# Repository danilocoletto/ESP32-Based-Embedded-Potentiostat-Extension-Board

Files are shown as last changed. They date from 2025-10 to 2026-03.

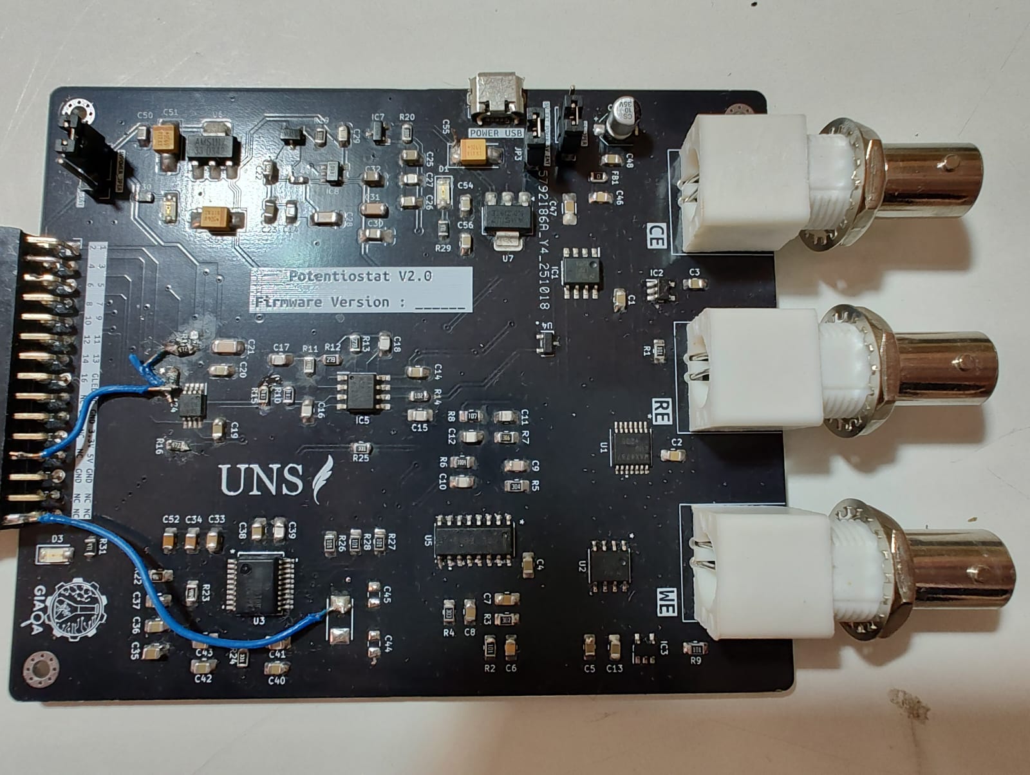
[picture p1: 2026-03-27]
Images&Schematics/Images/Potentiostat_PCB2.jpeg

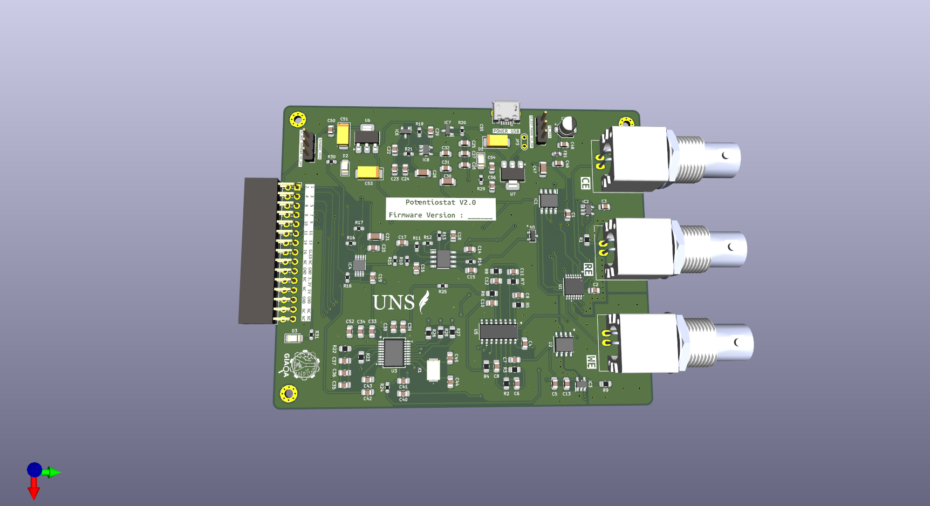
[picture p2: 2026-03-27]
Images&Schematics/Renders/Potenciostato_v2.0_1.png

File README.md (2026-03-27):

# ESP32-Based Real-Time Embedded Potentiostat Extension Board





> **⚠️ PROJECT STATUS: ONGOING**
> This project is currently under active development. The hardware design and firmware are subject to changes. Please check the `dev` branch for the latest updates.

## Key Features

- Real-time embedded architecture using **ESP32 + FreeRTOS**
- **24-bit precision ADC (ADS1255)** for nanoampere current measurements
- **16-bit DAC waveform generation** for electrochemical techniques
- Modular **analog front-end (AFE)** design
- Designed for **voltammetry and amperometry**
- **KiCad open hardware design**
- Firmware based on **ESP-IDF**

## 📖 Introduction

This repository contains the open-source hardware and firmware for a **Real-Time Embedded Potentiostat**. Designed as a high-precision **modular extension board**, this instrument allows for advanced electrochemical analysis (Voltammetry, Amperometry) in field applications.

A defining feature of this design is its **controller-agnostic modularity**. The board functions as a dedicated analog "backpack," decoupling the sensitive electrochemical front-end from the digital control logic. This architecture allows the board to be driven by various devices depending on the application needs:

* **ESP32 Implementation (Current Focus):** The primary implementation utilizes an **ESP32** microcontroller. This was chosen to provide **hard real-time execution** via FreeRTOS and to enable **wireless connectivity** (Wi-Fi/Bluetooth) for remote field monitoring in the future development.
* **External Instrumentation:** The header layout and signal routing were specifically designed to allow direct interfacing with test equipment such as the **Analog Discovery 2** (or similar oscilloscopes/logic analyzers). This allows user flexibility to to have alternative control strategies such as an ESP32, ATMEGA, STM32 or even an Analog Discovery.

### 💡 The Evolution: From Single-Board Computer to Real-Time Embedded
This project represents the **second generation** of the "All-in-One" potentiostat concept.

* **Previous Design (Generation 1):** Based on a **Raspberry Pi 3B+**. While it successfully integrated the user interface and control logic, the reliance on a non-real-time Operating System (Linux) introduced latency challenges for high-speed techniques. The usage of the ADS1110 (240 SPS) also limited the sweep speed.
* **Current Design (Generation 2):** Transitions to an **Embedded Real-Time Architecture**.
    * **Why?** To achieve **deterministic timing** and modular flexibility.
    * **Improvements:** Modular hardware design suitable for extension, significantly lower power consumption, reduced noise floor (nanoampere-level), and the ability to perform fast electrochemical screening without a heavy OS overhead.

## 🛠️ Hardware & Components

The hardware is designed to support nanoampere-level current measurements with a robust analog front-end.
- **KiCad PCB design**
- **MCU:** **ESP32-WROOM/WROVER** (Dual-core, 240 MHz). Handles waveform generation (DAC control), data acquisition (ADC readings), and wireless communication.
- **Analog Front-End (TIA + Control Amplifier):**
    - Improved topology using **High-Precision Rail-to-Rail OpAmps** (e.g., LMP770x Series and LM7721) for the Transimpedance Amplifier (TIA) and Control Amplifier.
    - **MAX4737:** Low-voltage, low on-resistance (RON), quad single-pole/single throw (SPST) analog switches.
    - **MAX4617:** High-Speed, Low-Voltage, CMOS Analog Multiplexers/Switches
- **ADS1255**: 24-bit ADC High-Speed ADC (replacing the slower ADS1110 of the previous version for an ADS1255) to support faster sweep rates (>1000 mV/s) and filter line noise at low current measurements.
- **MAX5217**: 16-bit DAC Low-Power with I2C/SPI interface for precise potential steps.
- **Power Management:** On-board LDOs and precision voltage references (2.500V / 5.000V) to ensure stable operation in field conditions.
- **Anti-Aliasing:** Active 4th-order Sallen-Key filtering to smooth signal steps and reduce noise.

## Firmware

- **ESP-IDF framework**
- **FreeRTOS tasks**
- **SPI driver for ADS1255**
- **I2C driver for DAC**
- **State machine for system management**
- **Baremetal libraries for precise timing during experiments**

## 📂 Repository Structure

The repository is organized as follows:

```
├── Diseno_3D/                          # Fusion360 project and .stl files for 3D case design
├── Hardware/                           # KiCad project files (Schematics, PCB Layout, BOM)
├── Images&Schematics/
│   ├── Images/
│   ├── Interface/
│   ├── Renders/
│   ├── Schematics/
├── Software/ 
│   ├── ESP32_Firmware/ 
│   │   ├── PotentiostatV2_Firmware/    # ESP-IDF C/C++ source code
│   │   │   ├── main/                   # Core logic (FreeRTOS tasks, State Machine)
│   │   │   ├── components/             # Drivers for DAC, ADC, and Potentiostat control
│   │   ├── Main/                       # GUI and Python Backend modules
│   │   │   ├── modules/                # Python backend modules
│   │   │   ├── logos/                  # logos folder
│   │   │   ├── gui/                    # Graphic User Interface .ui file
├── Información/                        # Datasheets and design notes
└── README.md                           # This file
```

## 🔌 Pinout & Interface

*> **Note:** As the PCB layout is being finalized, please refer to the schematic in the `Hardware` folder for the most up-to-date netlist. Below is the current configuration for the ESP32 implementation.*

### ⚡ Analog Front-End Connections
* **WE (Working Electrode):** Input for current measurement.
* **RE (Reference Electrode):** Feedback input (Shielded).
* **CE (Counter Electrode):** Current injection output.

### 🧩 ESP32 GPIO Mapping

| Component | Function | ESP32 GPIO | Description |
| :--- | :--- | :--- | :--- |
| **ADS1255 (ADC)** | **MISO** (DOUT) | **19** | SPI Data Input |
| | **MOSI** (DIN) | **23** | SPI Data Output |
| | **SCLK** | **18** | SPI Clock |
| | **CS** | **5** | Chip Select |
| | **DRDY** | **4** | Data Ready Interrupt |
| | **CLOCK** | **16** | (Optional) ADS1255 System Clock |
| **MAX5217 (DAC)** | **SDA** | **21** | I2C Data |
| | **SCL** | **22** | I2C Clock |
| | **NAUX** | **32** | Aux/Load Control |
| **MAX4617 (Mux)** | **SEL A** | **27** | Range/Gain Select Bit A |
| | **SEL B** | **26** | Range/Gain Select Bit B |
| | **SEL C** | **25** | Range/Gain Select Bit C |
| **MAX4737 (Switches)**| **CR SHORT EN**| **14** | Counter-Reference Short Enable |
| | **RE FB EN** | **33** | Reference Feedback Enable |
| | **WE EN** | **13** | Working Electrode Enable |
| | **CE EN** | **15** | Counter Electrode Enable |
| **Misc** | **GREEN LED** | **2** | Onboard Status LED (Green) |

## 📚 References & Context

For context on the theoretical background and the first generation of this device, please refer to our published article on the Raspberry Pi-based version:

> **(All-in-One) Open Source Potentiostat for Field Analysis Based on Raspberry Pi**
> *Hardware* 2024, 3(4), 17; [https://doi.org/10.3390/hardware3040017](https://www.mdpi.com/2813-6640/3/4/17)

Case Design:

> *3D Printed Design by [Boris Diaduch](https://www.linkedin.com/in/borisdiaduch/)*

---

*Maintained by [Ing. Danilo Coletto Gallego](www.linkedin.com/in/danilocoletto)*

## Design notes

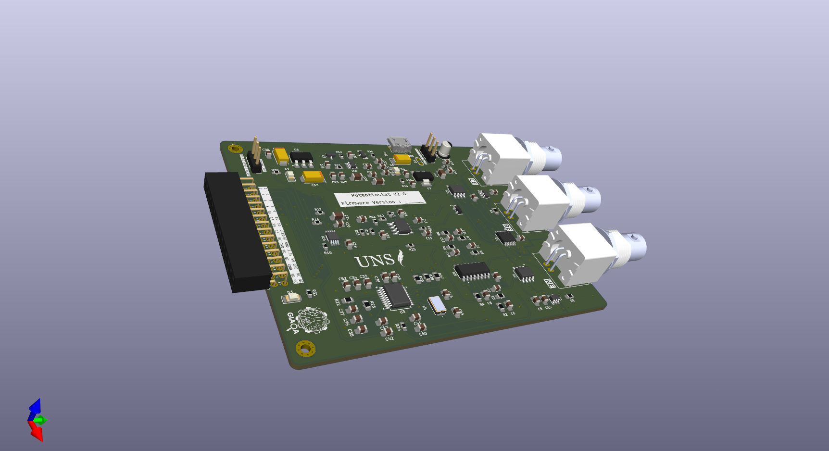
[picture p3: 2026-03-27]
Images&Schematics/Renders/Potenciostato_v2.0_2.png

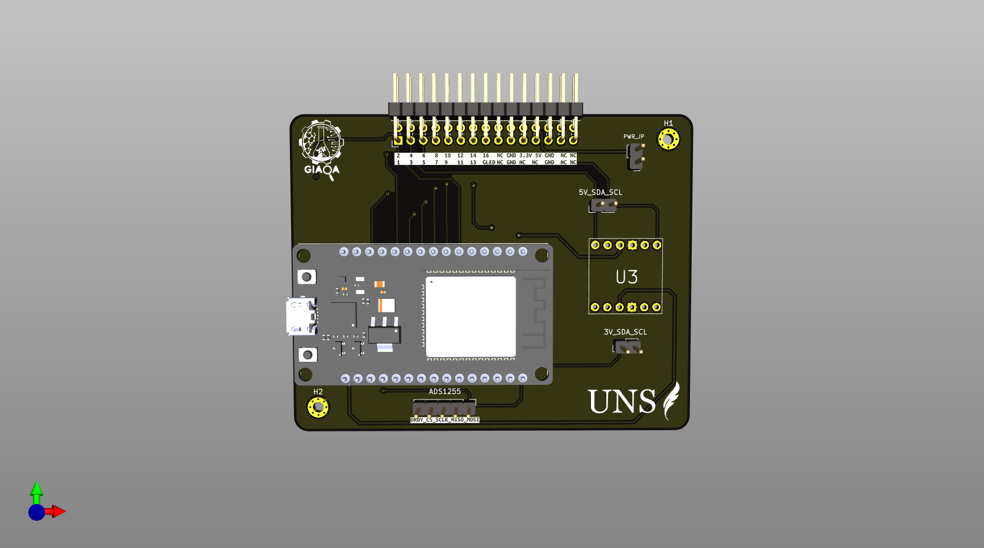
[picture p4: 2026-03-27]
Images&Schematics/Renders/ESP32_Board_3.png

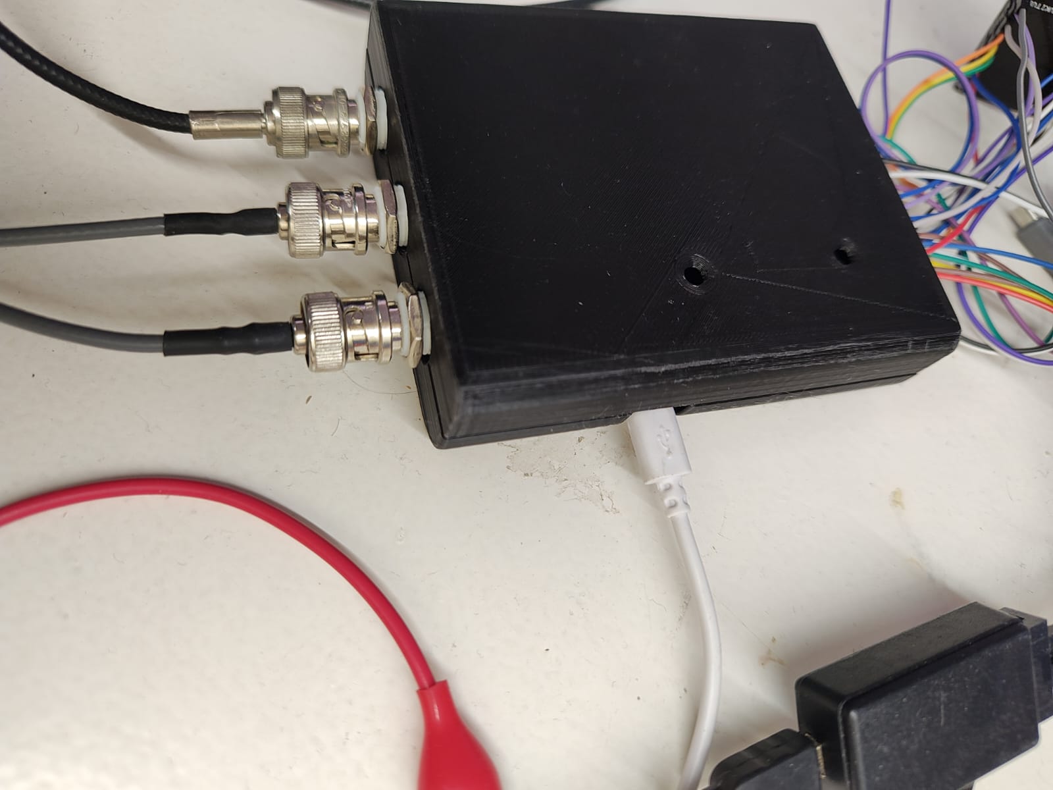
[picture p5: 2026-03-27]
Images&Schematics/Images/Potentiostat_Close_Case1.jpeg

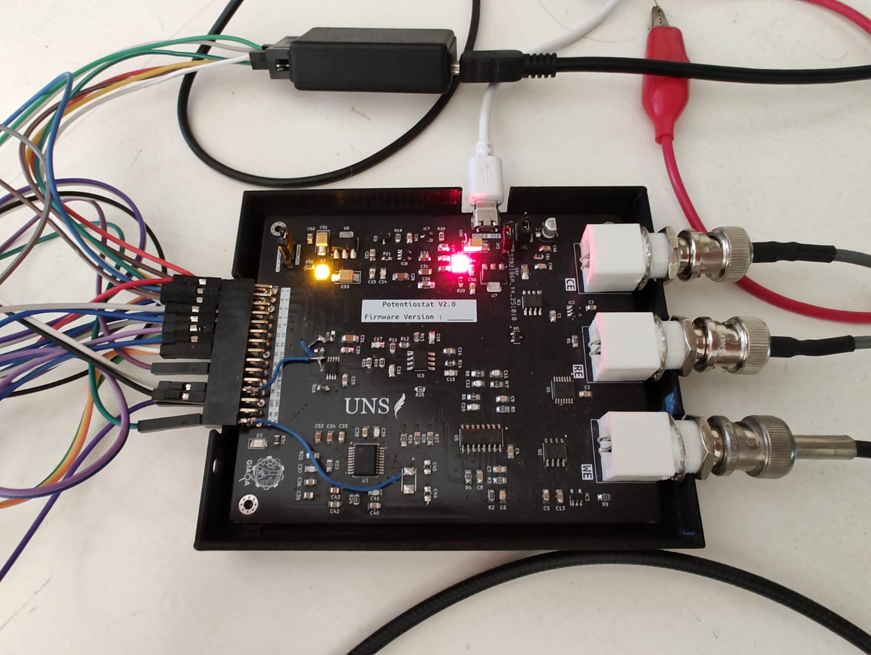
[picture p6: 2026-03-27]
Images&Schematics/Images/Potentiostat_Open_Case_ON.jpeg

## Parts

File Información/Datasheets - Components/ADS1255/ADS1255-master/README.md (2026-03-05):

# ADS1255 / ADS1256 Library

### Very Low Noise, 24-Bit Analog-to-Digital Converter

This library is made for the STM32 HAL (Hardware Abstraction Library) platform. The example code is for STM32CubeMX and Keil uVision 5 IDE.

> **Datasheet: [ti.com](https://www.ti.com/lit/ds/sbas288k/sbas288k.pdf?)**

---



### Usage

```c
/* USER CODE BEGIN Includes */
#include <ads1255.h>
```
```c
/* USER CODE BEGIN PV */
ADS125X_t adc1;
/* USER CODE END PV */

int main(void)
{
    /* USER CODE BEGIN 2 */
    adc1.csPort = SPI2_CS_GPIO_Port;
    adc1.csPin  = SPI2_CS_Pin;
    adc1.drdyPort = SPI2_DRDY_GPIO_Port;
    adc1.drdyPin  = SPI2_DRDY_Pin;
    adc1.vref = 2.5f;
    adc1.oscFreq = ADS125X_OSC_FREQ;
    
    printf("\n");
    printf("ADC config...\n");
    // 10 SPS / PGA=1 / buffer off
    ADS125X_Init(&adc1, &hspi2, ADS125X_DRATE_10SPS, ADS125X_PGA1, 0);
    printf("...done\n");
    /* USER CODE END 2 */

    /* Infinite loop */
    /* USER CODE BEGIN WHILE */
    while (1)
    {
    /* USER CODE END WHILE */

    /* USER CODE BEGIN 3 */
        float volt[2] = {0.0f, 0.0f};
        ADS125X_ChannelDiff_Set(&adc1, ADS125X_MUXP_AIN0, ADS125X_MUXN_AIN1);
        volt[0] = ADS125X_ADC_ReadVolt(&adc1);
        printf("%.15f\n", volt[0]);
        
        ADS125X_ChannelDiff_Set(&adc1, ADS125X_MUXP_AIN2, ADS125X_MUXN_AIN3);
        ADS125X_CMD_Send(&adc1, ADS125X_CMD_SYNC);
        volt[1] = ADS125X_ADC_ReadVolt(&adc1);
        printf("%.15f\n", volt[1]);
        
    }
    /* USER CODE END 3 */
}

```

---

### See Also

- [adienakhmad/ADS1256](https://github.com/adienakhmad/ADS1256)
- [Flydroid/ADS12xx-Library](https://github.com/Flydroid/ADS12xx-Library)
- [mbilsky/TeensyADS1256](https://github.com/mbilsky/TeensyADS1256)

---

### License 

Apache 2.0 

(c) 2022 eta Systems GmbH

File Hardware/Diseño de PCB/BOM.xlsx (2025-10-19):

Comment | Designator | Footprint | JLCPCB Part #
1kΩ@100MHz 800mA | FB1 | 603 | C279752

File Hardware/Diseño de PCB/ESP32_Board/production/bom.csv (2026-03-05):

Designator | Footprint | Quantity | Value | LCSC Part #
3V_SDA_SCL, 5V_SDA_SCL | PinHeader_1x02_P2.54mm_Vertical | 2 | Conn_01x02
ADS1255 | PinHeader_1x05_P2.54mm_Vertical | 1 | Conn_01x05
J1 | PinHeader_2x15_P2.54mm_Horizontal | 1 | Conn_02x15_Odd_Even
PWR_JP | PinHeader_1x02_P2.54mm_Vertical | 1 | Jumper_2_Open
U1 | MODULE_ESP32_DEVKIT_V1_CORRECTED | 1 | ESP32 - DEVKIT
U3 | LevelShifter | 1 | ~

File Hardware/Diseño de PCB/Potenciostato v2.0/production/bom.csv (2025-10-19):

Designator | Footprint | Quantity | Value | LCSC Part #
C1, C13, C14, C19, C20, C23, C26, C29, C3, C34, C36, C38, C4, C40, C42, C48, C5, C50, C52, C54, C56 | 0805 | 21 | 100n
C10 | 0805 | 1 | 2p
C11 | 0805 | 1 | 0.2p
C12 | 0805 | 1 | 0.1p
C15 | 0805 | 1 | 68p
C16 | 0805 | 1 | 160p
C17, C18 | 0805 | 2 | 180p
C2, C46 | 0805 | 2 | 10n
C21, C28 | 1206 | 2 | 1u
C22, C25, C32, C35 | 0805 | 4 | 47u
C24, C27, C37, C39, C41 | 0805 | 5 | 100p
C30 | 1206 | 1 | 100u
C31 | 0805 | 1 | 0.1u
C33, C43 | 0805 | 2 | 10u
C44, C45 | 0805 | 2 | 18p
C47 | 1206 | 1 | 2.2n
C49 | CP_Elec_4x5.4 | 1 | 10u
C51, C53, C55 | CP_EIA-6032-20_AVX-F_Pad2.25x2.35mm_HandSolder | 3 | 10u
C6 | 0805 | 1 | 56n
C7 | 0805 | 1 | 2n
C8 | 0805 | 1 | 200p
C9 | 0805 | 1 | 20p
D1 | 1206 | 1 | Red
D2 | 1206 | 1 | Yellow
D3 | 1206 | 1 | Green
FB1 | 0603 | 1 | FerriteBead_Small
IC1 | SOIC127P600X175_LMP7702 | 1 | LMP7702MAX_NOPB
IC2, IC3 | SOT95P280X145_LMP7701 | 2 | LMP7701MFX_NOPB
IC4 | SOP65P490X110_MAX5217 | 1 | MAX5217GUA+
IC5 | SOIC127P600X175_MAX4477 | 1 | MAX4477ASA+
IC6 | SOT95P237X112_LM40402_5 | 1 | LM4040AIM3X-2.5_NOPB
IC7 | SOT95P237X112_LM4040A5 | 1 | LM4040A50IDBZR
IC8 | SOT95P280X145_OPA354 | 1 | OPA354AIDBVT
J1, J3, J5 | BNC_Amphenol_B6252HB-NPP3G-50_Horizontal | 3 | Conn_Coaxial
J2 | PinSocket_2x15_P2.54mm_Horizontal | 1 | Conn_02x15_Odd_Even
J7 | USB_Micro-B_GCT_USB3076-30-A | 1 | USB_B_Micro
JP3 | TestPoint_2Pads_Pitch2.54mm_Drill0.8mm | 1 | Jumper_2_Open
R1, R2, R26, R27, R28, R9 | 0805 | 6 | 100
R10, R15 | 0603 | 2 | 18.7k
R11, R14, R19, R20 | 0603 | 4 | 1k
R12, R13 | 0603 | 2 | 25.5k
R16, R17, R18 | 0603 | 3 | 4.7k
R21 | 0603 | 1 | 10k
R22, R23 | 0805 | 2 | 49.9
R24, R25 | 0603 | 2 | 300
R29, R30, R31 | 0603 | 3 | 470
R3 | 0805 | 1 | 3k
R4 | 0805 | 1 | 30k
R5 | 0805 | 1 | 300k
R6 | 0805 | 1 | 3M
R7 | 0805 | 1 | 30M
R8 | 0805 | 1 | 100M
U1 | MAX4737 | 1 | MAX4737EUD+
U2 | M08ALMP7721_ | 1 | LMP7721MA/NOPB
U3 | DB20_ADS1255 | 1 | ADS1255IDBR
U4 | SOT23_5491 | 1 | MAX5491LA01000+T
U5 | MAX4617 | 1 | MAX4617CSE+
U6 | SOT-223-3_TabPin2 | 1 | AMS1117-3.3
U7 | SOT-223-3_TabPin2 | 1 | AMS1117-5.0
X1 | CRYSTAL_8 | 1 | XTAL8MHZ

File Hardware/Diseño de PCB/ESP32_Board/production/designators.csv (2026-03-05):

3V_SDA_SCL:1
5V_SDA_SCL:1
ADS1255:1
H1:1
H2:1
J1:1
KIBUZZARD-68F13266:1
KIBUZZARD-69A1DE73:1
KIBUZZARD-69A5AE09:1
PWR_JP:1
U1:1
U2:1
U3:1

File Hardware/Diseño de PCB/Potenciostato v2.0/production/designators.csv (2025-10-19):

C1:1
C10:1
C11:1
C12:1
C13:1
C14:1
C15:1
C16:1
C17:1
C18:1
C19:1
C2:1
C20:1
C21:1
C22:1
C23:1
C24:1
C25:1
C26:1
C27:1
C28:1
C29:1
C3:1
C30:1
C31:1
C32:1
C33:1
C34:1
C35:1
C36:1
C37:1
C38:1
C39:1
C4:1
C40:1
C41:1
C42:1
C43:1
C44:1
C45:1
C46:1
C47:1
C48:1
C49:1
C5:1
C50:1
C51:1
C52:1
C53:1
C54:1
C55:1
C56:1
C6:1
C7:1
C8:1
C9:1
D1:1
D2:1
D3:1
FB1:1
H1:1
H3:1
H4:1
IC1:1
IC2:1
IC3:1
IC4:1
IC5:1
IC6:1
IC7:1
IC8:1
J1:1
J2:1
J3:1
J5:1
J7:1
JP1:1
JP2:1
JP3:1
KIBUZZARD-68ED1B67:1
KIBUZZARD-68ED1EA7:1
KIBUZZARD-68ED1F3F:1
KIBUZZARD-68ED1F51:1
KIBUZZARD-68ED1F9A:1
KIBUZZARD-68ED3374:1
KIBUZZARD-68ED337E:1
KIBUZZARD-68ED3386:1
KIBUZZARD-68ED3787:1
KIBUZZARD-68F13228:1
KIBUZZARD-68F13266:1
R1:1
R10:1
R11:1
R12:1
R13:1
R14:1
R15:1
R16:1
R17:1
R18:1
R19:1
R2:1
R20:1
R21:1
R22:1
R23:1
R24:1
R25:1
R26:1
R27:1
R28:1
R29:1
R3:1
R30:1
R31:1
R4:1
R5:1
R6:1
R7:1
R8:1
R9:1
U1:1
U2:1
U3:1
U4:1
U5:1
U6:1
U7:1
X1:1

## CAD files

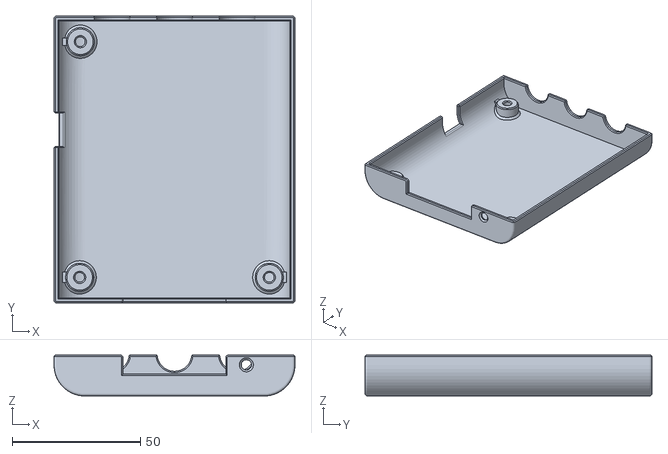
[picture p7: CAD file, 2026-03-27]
Diseno_3D/STL_Pot_Bot_Case2.stl
94.0 x 112.0 x 16.0

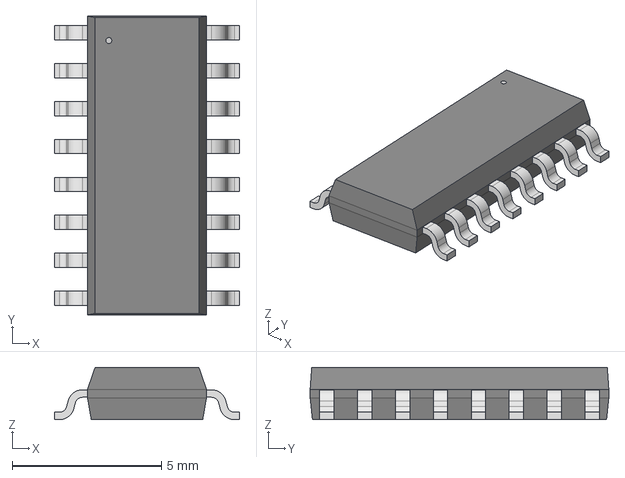
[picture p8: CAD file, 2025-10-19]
Hardware/Diseño de PCB/Potenciostato v2.0/3d_models/MAX4617CSE.step
6.20 x 10.0 x 1.75 mm

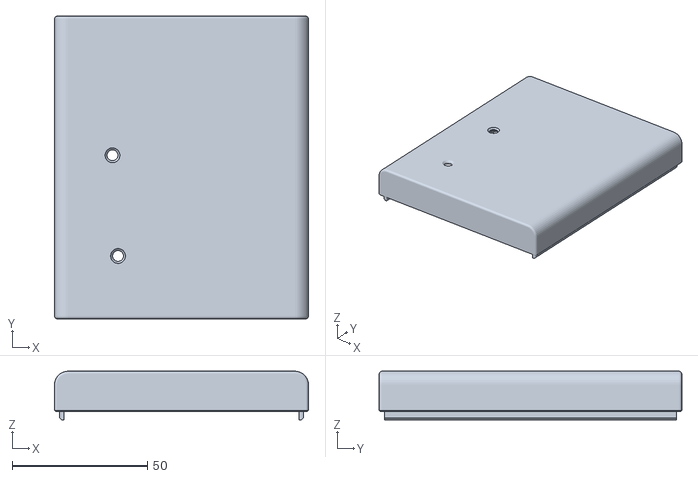
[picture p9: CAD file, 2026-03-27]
Diseno_3D/STL_Pot_Top_Case2.stl
94.0 x 112.0 x 18.0

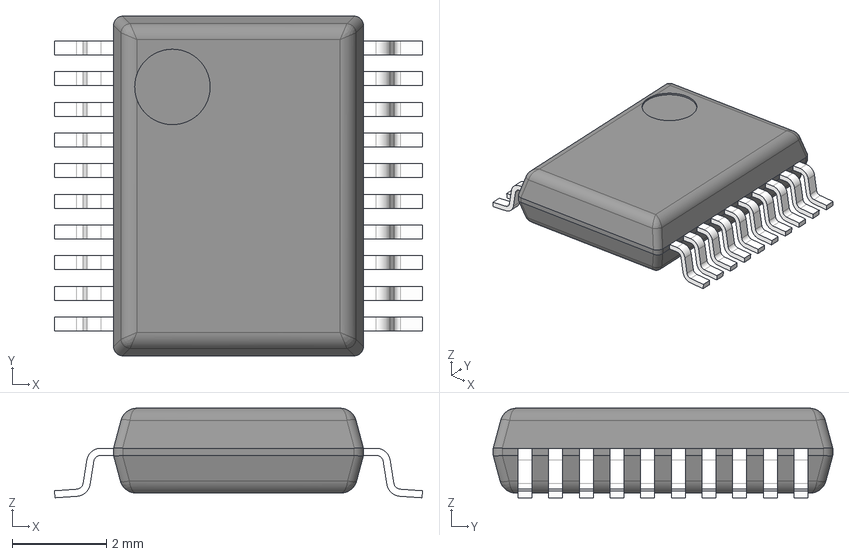
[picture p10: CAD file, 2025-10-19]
Hardware/Diseño de PCB/Potenciostato v2.0/3d_models/ADS1255.stp
7.80 x 7.20 x 1.90 mm
BODY-SSOP
LEAD-SSOP x 20
PIN1

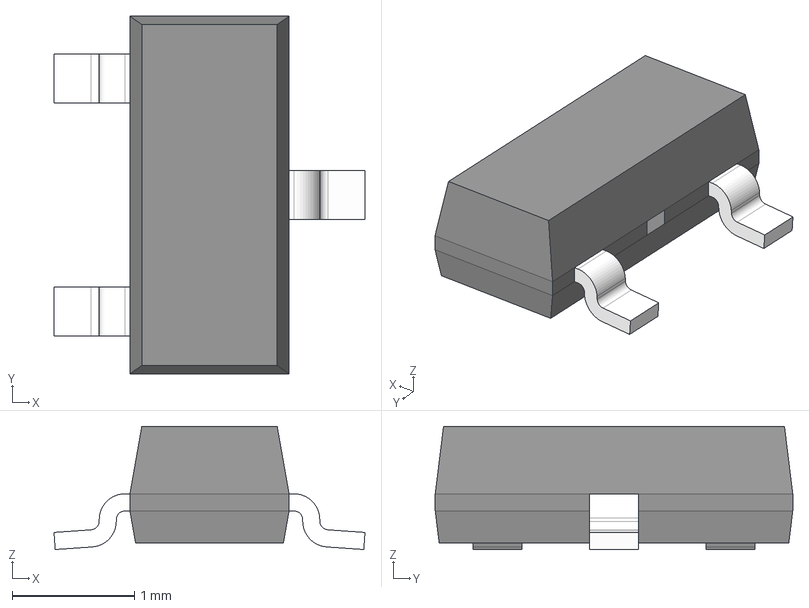
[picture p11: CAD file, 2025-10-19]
Hardware/Diseño de PCB/Potenciostato v2.0/3d_models/LM4040A50IDBZR.stp
2.54 x 2.92 x 1.01 mm
BODY-SOT
LEAD-SOT x 3
PIN1-ID
TIEBAR

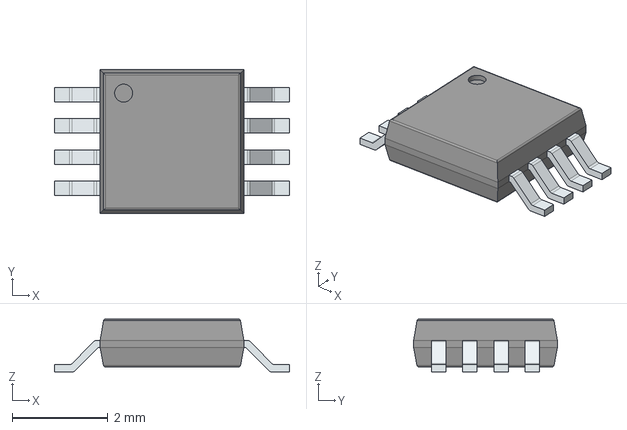
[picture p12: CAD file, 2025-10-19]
Hardware/Diseño de PCB/Potenciostato v2.0/3d_models/MAX5217GUA+.stp
4.91 x 3.00 x 1.10 mm
PinsArrayLR

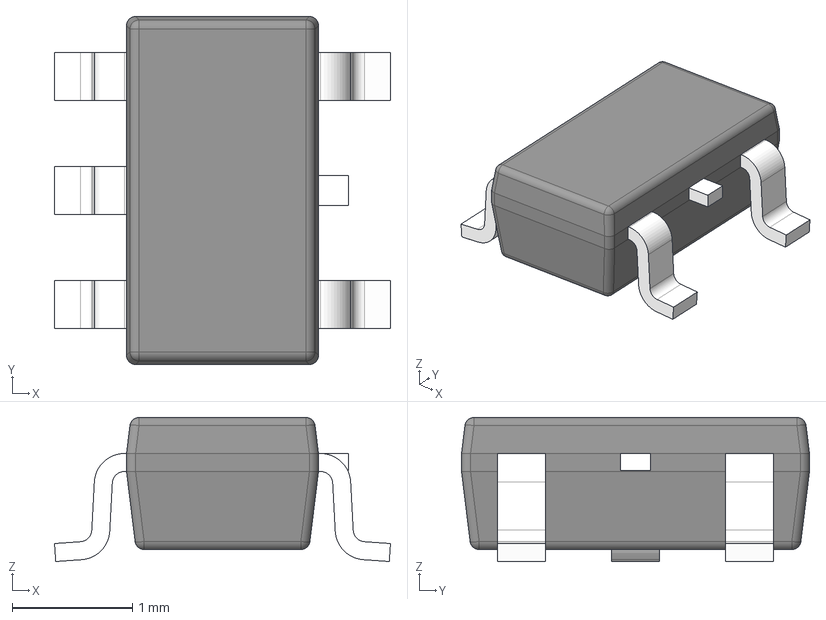
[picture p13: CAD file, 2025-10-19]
Hardware/Diseño de PCB/Potenciostato v2.0/3d_models/OPA354AIDBVT.stp
2.80 x 2.90 x 1.20 mm
BODY-SOT
LEAD-SOT x 5
LEAD-DUMMY

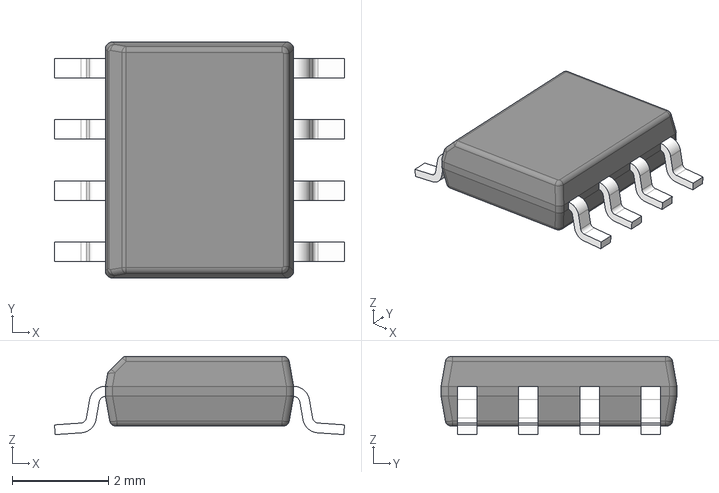
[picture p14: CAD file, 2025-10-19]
Hardware/Diseño de PCB/Potenciostato v2.0/3d_models/OPA2320AIDR.stp
6.02 x 4.90 x 1.63 mm
BODY-SO
LEAD-D0008A x 8

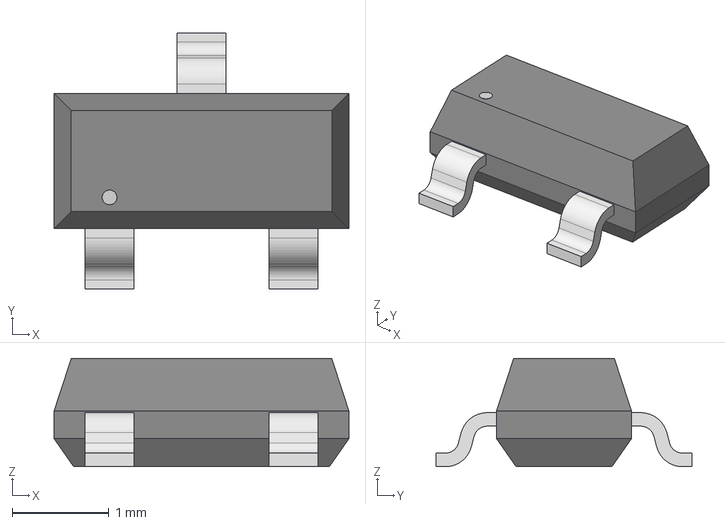
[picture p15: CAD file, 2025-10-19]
Hardware/Diseño de PCB/Potenciostato v2.0/3d_models/MAX5491LA01000.step
3.05 x 2.64 x 1.12 mm

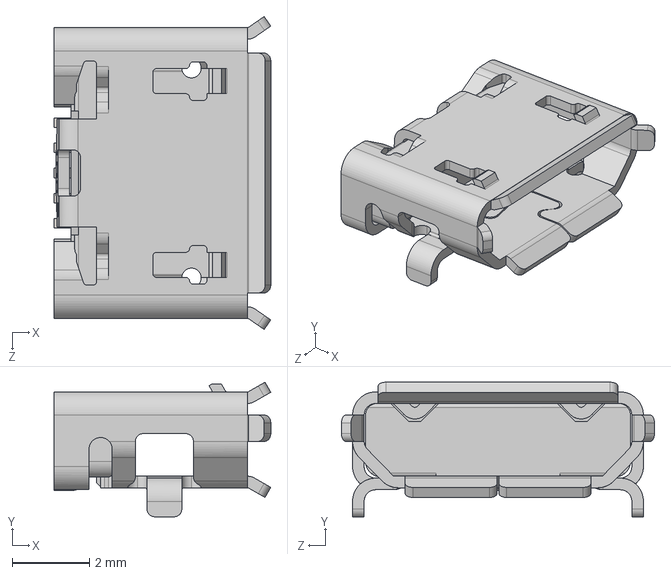
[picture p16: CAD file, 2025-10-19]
Hardware/Diseño de PCB/Potenciostato v2.0/3d_models/USB_MicroB.stp
5.60 x 3.48 x 8.09 mm

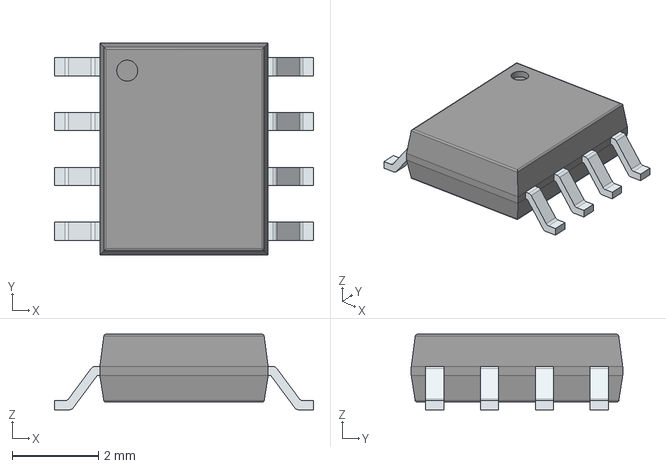
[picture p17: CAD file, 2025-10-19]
Hardware/Diseño de PCB/Potenciostato v2.0/3d_models/MAX4477ASA+.stp
6.00 x 4.90 x 1.75 mm
PinsArrayLR

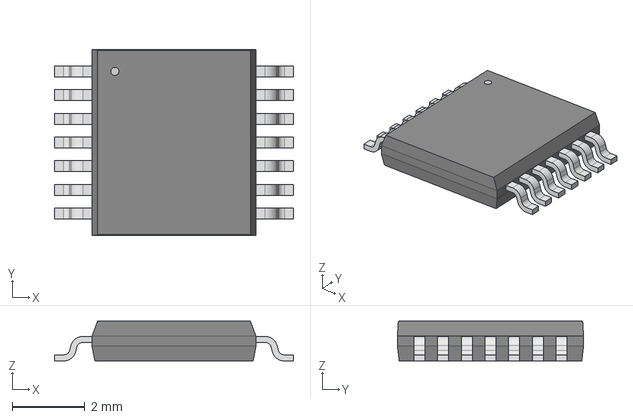
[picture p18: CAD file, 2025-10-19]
Hardware/Diseño de PCB/Potenciostato v2.0/3d_models/MAX4737.step
6.55 x 5.11 x 1.09 mm

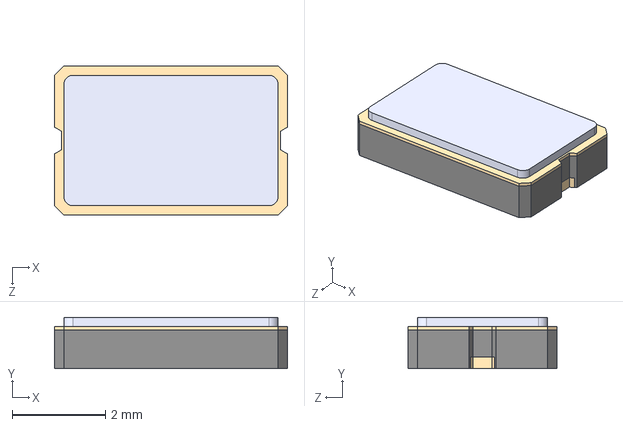
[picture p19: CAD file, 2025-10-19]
Hardware/Diseño de PCB/Potenciostato v2.0/3d_models/ECS-80-18-30Q-VY-TR.stp
5.00 x 1.10 x 3.20 mm

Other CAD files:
Diseno_3D/Potentiostat_Case.f3d

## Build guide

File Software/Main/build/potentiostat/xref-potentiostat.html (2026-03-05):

# modulegraph cross reference for main.py, pyi_rth_inspect.py, pyi_rth_multiprocessing.py, pyi_rth_pkgutil.py, pyi_rth_pyqt6.py, pyi_rth_pyqtgraph_multiprocess.py

main.py Script

imports: PyQt6 • PyQt6.QtCore • PyQt6.QtGui • PyQt6.QtWidgets • PyQt6.uic • PyQt6.uic.load_ui • PyQt6.uic.uiparser • _collections_abc • _weakrefset • abc • codecs • collections • controller • copyreg • ctypes • encodings • encodings._win_cp_codecs • encodings.aliases • encodings.ascii • encodings.base64_codec • encodings.big5 • encodings.big5hkscs • encodings.bz2_codec • encodings.charmap • encodings.cp037 • encodings.cp1006 • encodings.cp1026 • encodings.cp1125 • encodings.cp1140 • encodings.cp1250 • encodings.cp1251 • encodings.cp1252 • encodings.cp1253 • encodings.cp1254 • encodings.cp1255 • encodings.cp1256 • encodings.cp1257 • encodings.cp1258 • encodings.cp273 • encodings.cp424 • encodings.cp437 • encodings.cp500 • encodings.cp720 • encodings.cp737 • encodings.cp775 • encodings.cp850 • encodings.cp852 • encodings.cp855 • encodings.cp856 • encodings.cp857 • encodings.cp858 • encodings.cp860 • encodings.cp861 • encodings.cp862 • encodings.cp863 • encodings.cp864 • encodings.cp865 • encodings.cp866 • encodings.cp869 • encodings.cp874 • encodings.cp875 • encodings.cp932 • encodings.cp949 • encodings.cp950 • encodings.euc_jis_2004 • encodings.euc_jisx0213 • encodings.euc_jp • encodings.euc_kr • encodings.gb18030 • encodings.gb2312 • encodings.gbk • encodings.hex_codec • encodings.hp_roman8 • encodings.hz • encodings.idna • encodings.iso2022_jp • encodings.iso2022_jp_1 • encodings.iso2022_jp_2 • encodings.iso2022_jp_2004 • encodings.iso2022_jp_3 • encodings.iso2022_jp_ext • encodings.iso2022_kr • encodings.iso8859_1 • encodings.iso8859_10 • encodings.iso8859_11 • encodings.iso8859_13 • encodings.iso8859_14 • encodings.iso8859_15 • encodings.iso8859_16 • encodings.iso8859_2 • encodings.iso8859_3 • encodings.iso8859_4 • encodings.iso8859_5 • encodings.iso8859_6 • encodings.iso8859_7 • encodings.iso8859_8 • encodings.iso8859_9 • encodings.johab • encodings.koi8_r • encodings.koi8_t • encodings.koi8_u • encodings.kz1048 • encodings.latin_1 • encodings.mac_arabic • encodings.mac_croatian • encodings.mac_cyrillic • encodings.mac_farsi • encodings.mac_greek • encodings.mac_iceland • encodings.mac_latin2 • encodings.mac_roman • encodings.mac_romanian • encodings.mac_turkish • encodings.mbcs • encodings.oem • encodings.palmos • encodings.ptcp154 • encodings.punycode • encodings.quopri_codec • encodings.raw_unicode_escape • encodings.rot_13 • encodings.shift_jis • encodings.shift_jis_2004 • encodings.shift_jisx0213 • encodings.tis_620 • encodings.undefined • encodings.unicode_escape • encodings.utf_16 • encodings.utf_16_be • encodings.utf_16_le • encodings.utf_32 • encodings.utf_32_be • encodings.utf_32_le • encodings.utf_7 • encodings.utf_8 • encodings.utf_8_sig • encodings.uu_codec • encodings.zlib_codec • enum • functools • genericpath • heapq • io • keyword • linecache • locale • logging • modules • modules.data_viewer • modules.processor • modules.protocol_defs • modules.serial_manager • modules.utils • ntpath • numpy • numpy.core • operator • os • posixpath • pyi_rth_inspect.py • pyi_rth_multiprocessing.py • pyi_rth_pkgutil.py • pyi_rth_pyqt6.py • pyi_rth_pyqtgraph_multiprocess.py • pyqtgraph • pyqtgraph.exporters • pyqtgraph.exporters.ImageExporter • pyqtgraph.exporters.SVGExporter • pyqtgraph.graphicsItems • pyqtgraph.graphicsItems.LegendItem • pyqtgraph.graphicsItems.PlotItem • re • re._casefix • re._compiler • re._constants • re._parser • reprlib • scipy • scipy.fft • scipy.signal • scipy.signal._filter_design • serial • serial.tools • serial.tools.list_ports • serial.tools.list_ports_common • serial.tools.list_ports_windows • sre_compile • sre_constants • sre_parse • stat • sys • traceback • types • unittest • unittest.case • unittest.loader • unittest.runner • unittest.signals • unittest.suite • warnings • weakref

pyi_rth_inspect.py Script

imports: inspect • os • sys • zipfile

imported by: main.py

pyi_rth_multiprocessing.py Script

imports: multiprocessing • multiprocessing.spawn • subprocess • sys

imported by: main.py

pyi_rth_pkgutil.py Script

imports: pkgutil • pyimod02_importers

imported by: main.py

pyi_rth_pyqt6.py Script

imports: _pyi_rth_utils • _pyi_rth_utils.qt • os • sys

imported by: main.py

pyi_rth_pyqtgraph_multiprocess.py Script

imports: importlib.util • os • sys

imported by: main.py

'System.IO' MissingModule

imported by: serial.serialcli

'collections.abc' MissingModule

imported by: _colorize • _pyrepl.types • asyncio.base_events • asyncio.coroutines • http.client • importlib.resources.readers • inspect • logging • multiprocessing.managers • numpy._typing._array_like • numpy._typing._dtype_like • numpy._typing._nested_sequence • numpy._typing._shape • numpy.lib._function_base_impl • numpy.lib._npyio_impl • numpy.polynomial._polybase • numpy.random._common • numpy.random._generator • numpy.random.bit_generator • numpy.random.mtrand • pyqtgraph.colormap • pyqtgraph.graphicsItems.ImageItem • pyqtgraph.graphicsItems.PlotItem.PlotItem • scipy._lib._array_api • scipy._lib._docscrape • scipy._lib.array_api_compat._internal • scipy._lib.array_api_compat.common._aliases • scipy._lib.array_api_compat.common._fft • scipy._lib.array_api_compat.common._helpers • scipy._lib.array_api_compat.common._typing • scipy._lib.array_api_compat.dask.array._aliases • scipy._lib.array_api_compat.torch._aliases • scipy._lib.array_api_extra._delegation • scipy._lib.array_api_extra._lib._at • scipy._lib.array_api_extra._lib._funcs • scipy._lib.array_api_extra._lib._lazy • scipy._lib.array_api_extra._lib._utils._helpers • scipy._lib.array_api_extra.testing • scipy._lib.doccer • scipy._lib.pyprima • scipy.constants._codata • scipy.integrate._quadrature • scipy.linalg._decomp_cossin • scipy.ndimage._filters • scipy.ndimage._ni_support • scipy.signal._short_time_fft • scipy.spatial.distance • scipy.spatial.transform._rigid_transform • scipy.spatial.transform._rotation • scipy.special._support_alternative_backends • scipy.stats._continuous_distns • scipy.stats._multicomp • scipy.stats._qmc • scipy.stats._resampling • scipy.stats._sensitivity_analysis • scipy.stats._stats_py • selectors • traceback • tracemalloc • typing • xml.etree.ElementTree

'cupy.cuda' MissingModule

imported by: scipy._lib.array_api_compat.cupy._typing

'dask.array' MissingModule

imported by: scipy._lib.array_api_compat.common._helpers • scipy._lib.array_api_compat.dask.array._aliases • scipy._lib.array_api_compat.dask.array._info • scipy._lib.array_api_extra.testing

'dask.typing' MissingModule

imported by: scipy._lib.array_api_extra.testing

'java.lang' MissingModule

imported by: platform

'jax.experimental' MissingModule

imported by: scipy._lib.array_api_compat.common._helpers

'jax.nn' MissingModule

imported by: scipy._lib.array_api_extra._delegation

'jax.numpy' MissingModule

imported by: scipy._lib.array_api_compat.common._helpers

'matplotlib.backends' MissingModule

imported by: pyqtgraph.widgets.MatplotlibWidget

'matplotlib.collections' MissingModule

imported by: scipy.spatial._plotutils

'matplotlib.figure' MissingModule

imported by: pyqtgraph.widgets.MatplotlibWidget

'matplotlib.pyplot' MissingModule

imported by: pyqtgraph.colormap • scipy.spatial._plotutils • scipy.stats._distribution_infrastructure • scipy.stats._fit • scipy.stats._survival

'matplotlib.ticker' MissingModule

imported by: scipy.stats._fit

'numpy_distutils.command' MissingModule

imported by: numpy.f2py.diagnose

'numpy_distutils.cpuinfo' MissingModule

imported by: numpy.f2py.diagnose

'numpy_distutils.fcompiler' MissingModule

imported by: numpy.f2py.diagnose

'scikits.umfpack' MissingModule

imported by: scipy.optimize._linprog_ip

'sksparse.cholmod' MissingModule

imported by: scipy.optimize._linprog_ip

'torch.nn' MissingModule

imported by: scipy._lib.array_api_extra._delegation

Cython MissingModule

imported by: scipy._lib._testutils

PyQt6 Package

imports: PyQt6.QtCore • PyQt6.QtGui • PyQt6.QtOpenGL • PyQt6.QtOpenGLWidgets • PyQt6.QtSvg • PyQt6.QtTest • PyQt6.QtWidgets • PyQt6.sip • PyQt6.uic • os • pkgutil • sys

imported by: PyQt6.QtCore • PyQt6.QtGui • PyQt6.QtOpenGL • PyQt6.QtOpenGLWidgets • PyQt6.QtSvg • PyQt6.QtTest • PyQt6.QtWidgets • PyQt6.sip • PyQt6.uic • PyQt6.uic.Loader.loader • PyQt6.uic.Loader.qobjectcreator • PyQt6.uic.load_ui • controller • main.py • pyqtgraph.Qt

PyQt6.QtCore C:\Users\danil\AppData\Local\Programs\Python\Python314\Lib\site-packages\PyQt6\QtCore.pyd

imports: PyQt6 • PyQt6.sip • collections • datetime • enum • re • typing • warnings

imported by: PyQt6 • PyQt6.QtGui • PyQt6.QtOpenGL • PyQt6.QtOpenGLWidgets • PyQt6.QtSvg • PyQt6.QtTest • PyQt6.QtWidgets • PyQt6.uic.Loader.loader • PyQt6.uic.compile_ui • controller • main.py • modules.data_viewer • modules.serial_manager • pyqtgraph.Qt

PyQt6.QtGui C:\Users\danil\AppData\Local\Programs\Python\Python314\Lib\site-packages\PyQt6\QtGui.pyd

imports: PyQt6 • PyQt6.QtCore • PyQt6.sip • collections • datetime • enum • re • typing • warnings

imported by: PyQt6 • PyQt6.QtOpenGL • PyQt6.QtOpenGLWidgets • PyQt6.QtSvg • PyQt6.QtTest • PyQt6.QtWidgets • PyQt6.uic.Loader.loader • PyQt6.uic.Loader.qobjectcreator • main.py • modules.data_viewer • pyqtgraph.Qt

PyQt6.QtOpenGL C:\Users\danil\AppData\Local\Programs\Python\Python314\Lib\site-packages\PyQt6\QtOpenGL.pyd

imports: PyQt6 • PyQt6.QtCore • PyQt6.QtGui • PyQt6.sip • collections • datetime • enum • re • typing • warnings

imported by: PyQt6 • PyQt6.QtOpenGLWidgets

PyQt6.QtOpenGLWidgets C:\Users\danil\AppData\Local\Programs\Python\Python314\Lib\site-packages\PyQt6\QtOpenGLWidgets.pyd

imports: PyQt6 • PyQt6.QtCore • PyQt6.QtGui • PyQt6.QtOpenGL • PyQt6.QtWidgets • PyQt6.sip • collections • datetime • enum • re • typing • warnings

imported by: PyQt6 • pyqtgraph.Qt

PyQt6.QtSvg C:\Users\danil\AppData\Local\Programs\Python\Python314\Lib\site-packages\PyQt6\QtSvg.pyd

imports: PyQt6 • PyQt6.QtCore • PyQt6.QtGui • PyQt6.sip • collections • datetime • enum • re • typing • warnings

imported by: PyQt6 • pyqtgraph.Qt

PyQt6.QtTest C:\Users\danil\AppData\Local\Programs\Python\Python314\Lib\site-packages\PyQt6\QtTest.pyd

imports: PyQt6 • PyQt6.QtCore • PyQt6.QtGui • PyQt6.QtWidgets • PyQt6.sip • collections • datetime • enum • re • typing • warnings

imported by: PyQt6 • pyqtgraph.Qt

PyQt6.QtWidgets C:\Users\danil\AppData\Local\Programs\Python\Python314\Lib\site-packages\PyQt6\QtWidgets.pyd

imports: PyQt6 • PyQt6.QtCore • PyQt6.QtGui • PyQt6.sip • collections • datetime • enum • re • typing • warnings

imported by: PyQt6 • PyQt6.QtOpenGLWidgets • PyQt6.QtTest • PyQt6.uic.Loader.loader • PyQt6.uic.Loader.qobjectcreator • PyQt6.uic.load_ui • controller • main.py • modules.data_viewer • pyqtgraph.Qt

PyQt6.sip C:\Users\danil\AppData\Local\Programs\Python\Python314\Lib\site-packages\PyQt6\sip.cp314-win_amd64.pyd

imports: PyQt6 • typing

imported by: PyQt6 • PyQt6.QtCore • PyQt6.QtGui • PyQt6.QtOpenGL • PyQt6.QtOpenGLWidgets • PyQt6.QtSvg • PyQt6.QtTest • PyQt6.QtWidgets • pyqtgraph.Qt

PyQt6.uic Package

imports: PyQt6 • PyQt6.uic.compile_ui • PyQt6.uic.load_ui • PyQt6.uic.objcreator • PyQt6.uic.ui_file

imported by: PyQt6 • PyQt6.uic.Compiler • PyQt6.uic.Loader • PyQt6.uic.compile_ui • PyQt6.uic.enum_map • PyQt6.uic.exceptions • PyQt6.uic.icon_cache • PyQt6.uic.load_ui • PyQt6.uic.objcreator • PyQt6.uic.properties • PyQt6.uic.ui_file • PyQt6.uic.uiparser • main.py • pyqtgraph.Qt

PyQt6.uic.Compiler Package

imports: PyQt6.uic • PyQt6.uic.Compiler • PyQt6.uic.Compiler.compiler • PyQt6.uic.Compiler.indenter • PyQt6.uic.Compiler.qtproxies

imported by: PyQt6.uic.Compiler • PyQt6.uic.Compiler.as_string • PyQt6.uic.Compiler.compiler • PyQt6.uic.Compiler.indenter • PyQt6.uic.Compiler.misc • PyQt6.uic.Compiler.proxy_metaclass • PyQt6.uic.Compiler.qobjectcreator • PyQt6.uic.Compiler.qtproxies • PyQt6.uic.compile_ui • PyQt6.uic.load_ui

PyQt6.uic.Compiler.as_string SourceModule

imports: PyQt6.uic.Compiler • re

imported by: PyQt6.uic.Compiler.qobjectcreator • PyQt6.uic.Compiler.qtproxies

PyQt6.uic.Compiler.compiler SourceModule

imports: PyQt6.uic.Compiler • PyQt6.uic.Compiler.indenter • PyQt6.uic.Compiler.qobjectcreator • PyQt6.uic.Compiler.qtproxies • PyQt6.uic.properties • PyQt6.uic.uiparser • sys

imported by: PyQt6.uic.Compiler • PyQt6.uic.compile_ui • PyQt6.uic.load_ui

PyQt6.uic.Compiler.indenter SourceModule

imports: PyQt6.uic.Compiler

imported by: PyQt6.uic.Compiler • PyQt6.uic.Compiler.compiler • PyQt6.uic.Compiler.qobjectcreator • PyQt6.uic.Compiler.qtproxies • PyQt6.uic.compile_ui

PyQt6.uic.Compiler.misc SourceModule

imports: PyQt6.uic.Compiler

imported by: PyQt6.uic.Compiler.proxy_metaclass • PyQt6.uic.Compiler.qtproxies

PyQt6.uic.Compiler.proxy_metaclass SourceModule

imports: PyQt6.uic.Compiler • PyQt6.uic.Compiler.misc • PyQt6.uic.Compiler.qtproxies

imported by: PyQt6.uic.Compiler.qtproxies

PyQt6.uic.Compiler.qobjectcreator SourceModule

imports: PyQt6.uic.Compiler • PyQt6.uic.Compiler.as_string • PyQt6.uic.Compiler.indenter • PyQt6.uic.Compiler.qtproxies • logging • sys

imported by: PyQt6.uic.Compiler.compiler

PyQt6.uic.Compiler.qtproxies SourceModule

imports: PyQt6.uic.Compiler • PyQt6.uic.Compiler.as_string • PyQt6.uic.Compiler.indenter • PyQt6.uic.Compiler.misc • PyQt6.uic.Compiler.proxy_metaclass • re • sys

imported by: PyQt6.uic.Compiler • PyQt6.uic.Compiler.compiler • PyQt6.uic.Compiler.proxy_metaclass • PyQt6.uic.Compiler.qobjectcreator

PyQt6.uic.Loader Package

imports: PyQt6.uic

imported by: PyQt6.uic.Loader.loader • PyQt6.uic.Loader.qobjectcreator

PyQt6.uic.Loader.loader SourceModule

imports: PyQt6 • PyQt6.QtCore • PyQt6.QtGui • PyQt6.QtWidgets • PyQt6.uic.Loader • PyQt6.uic.Loader.qobjectcreator • PyQt6.uic.uiparser

imported by: PyQt6.uic.load_ui

PyQt6.uic.Loader.qobjectcreator SourceModule

imports: PyQt6 • PyQt6.QtGui • PyQt6.QtWidgets • PyQt6.uic.Loader • sys

imported by: PyQt6.uic.Loader.loader

PyQt6.uic.compile_ui SourceModule

imports: PyQt6.QtCore • PyQt6.uic • PyQt6.uic.Compiler • PyQt6.uic.Compiler.compiler • PyQt6.uic.Compiler.indenter • concurrent.futures • functools • os

imported by: PyQt6.uic

PyQt6.uic.enum_map SourceModule

imports: PyQt6.uic

imported by: PyQt6.uic.properties

PyQt6.uic.exceptions SourceModule

imports: PyQt6.uic

imported by: PyQt6.uic.objcreator • PyQt6.uic.properties • PyQt6.uic.ui_file

PyQt6.uic.icon_cache SourceModule

imports: PyQt6.uic • os.path

imported by: PyQt6.uic.properties

PyQt6.uic.load_ui SourceModule

imports: PyQt6 • PyQt6.QtWidgets • PyQt6.uic • PyQt6.uic.Compiler • PyQt6.uic.Compiler.compiler • PyQt6.uic.Loader.loader • io • sys

imported by: PyQt6.uic • main.py

PyQt6.uic.objcreator SourceModule

imports: PyQt6.uic • PyQt6.uic.exceptions • os.path

imported by: PyQt6.uic • PyQt6.uic.uiparser

PyQt6.uic.properties SourceModule

imports: PyQt6.uic • PyQt6.uic.enum_map • PyQt6.uic.exceptions • PyQt6.uic.icon_cache • logging • os.path • sys

imported by: PyQt6.uic.Compiler.compiler • PyQt6.uic.uiparser

PyQt6.uic.ui_file SourceModule

imports: PyQt6.uic • PyQt6.uic.exceptions • xml.etree • xml.etree.ElementTree

imported by: PyQt6.uic • PyQt6.uic.uiparser

PyQt6.uic.uiparser SourceModule

imports: PyQt6.uic • PyQt6.uic.objcreator • PyQt6.uic.properties • PyQt6.uic.ui_file • logging • os • re • sys • xml.etree.ElementTree

imported by: PyQt6.uic.Compiler.compiler • PyQt6.uic.Loader.loader • main.py

System MissingModule

imported by: serial.serialcli

__future__ SourceModule

imported by: _pyrepl.pager • _pyrepl.trace • _pyrepl.utils • codeop • doctest • importlib.metadata • importlib.metadata._meta • importlib.resources.readers • pydoc • pyqtgraph.debug • pyqtgraph.reload • scipy._lib.array_api_compat.common._aliases • scipy._lib.array_api_compat.common._fft • scipy._lib.array_api_compat.common._helpers • scipy._lib.array_api_compat.common._linalg • scipy._lib.array_api_compat.common._typing • scipy._lib.array_api_compat.cupy._aliases • scipy._lib.array_api_compat.cupy._typing • scipy._lib.array_api_compat.dask.array._aliases • scipy._lib.array_api_compat.dask.array._info • scipy._lib.array_api_compat.numpy._aliases • scipy._lib.array_api_compat.numpy._info • scipy._lib.array_api_compat.numpy._typing • scipy._lib.array_api_compat.numpy.linalg • scipy._lib.array_api_compat.torch._aliases • scipy._lib.array_api_extra._lib._at • scipy._lib.array_api_extra._lib._lazy • scipy._lib.array_api_extra._lib._utils._helpers • scipy._lib.array_api_extra.testing • scipy.signal._signaltools • scipy.spatial.transform._rigid_transform • scipy.spatial.transform._rotation • serial • serial.serialcli • serial.serialjava • serial.serialposix • serial.serialutil • serial.serialwin32 • serial.tools.list_ports • serial.tools.list_ports_common • serial.tools.list_ports_linux • serial.tools.list_ports_osx • serial.tools.list_ports_posix • serial.tools.list_ports_windows • serial.win32 • shiboken6.Shiboken

_abc (builtin module)

imported by: abc

_aix_support SourceModule

imports: contextlib • os • subprocess • sys • sysconfig

imported by: sysconfig

_ast (builtin module)

imported by: _ast_unparse • ast

_ast_unparse SourceModule

imports: _ast • ast • contextlib • enum • sys

imported by: ast

_asyncio C:\Users\danil\AppData\Local\Programs\Python\Python314\DLLs\_asyncio.pyd

imported by: asyncio.events • asyncio.futures • asyncio.tasks

_bisect (builtin module)

imported by: bisect

_blake2 (builtin module)

imported by: hashlib

_bz2 C:\Users\danil\AppData\Local\Programs\Python\Python314\DLLs\_bz2.pyd

imported by: bz2

_codecs (builtin module)

imported by: codecs

_codecs_cn (builtin module)

imported by: encodings.gb18030 • encodings.gb2312 • encodings.gbk • encodings.hz

_codecs_hk (builtin module)

imported by: encodings.big5hkscs

_codecs_iso2022 (builtin module)

imported by: encodings.iso2022_jp • encodings.iso2022_jp_1 • encodings.iso2022_jp_2 • encodings.iso2022_jp_2004 • encodings.iso2022_jp_3 • encodings.iso2022_jp_ext • encodings.iso2022_kr

_codecs_jp (builtin module)

imported by: encodings.cp932 • encodings.euc_jis_2004 • encodings.euc_jisx0213 • encodings.euc_jp • encodings.shift_jis • encodings.shift_jis_2004 • encodings.shift_jisx0213

_codecs_kr (builtin module)

imported by: encodings.cp949 • encodings.euc_kr • encodings.johab

_codecs_tw (builtin module)

imported by: encodings.big5 • encodings.cp950

_collections (builtin module)

imported by: collections • threading

_collections_abc SourceModule

imports: abc • annotationlib • sys • warnings

imported by: collections • contextlib • contextvars • io • locale • main.py • os • pathlib • random • types • weakref

_colorize SourceModule

imports: 'collections.abc' • dataclasses • io • nt • os • sys • typing

imported by: _pyrepl.utils • argparse • calendar • doctest • pdb • traceback • unittest.result • unittest.runner

_compat_pickle SourceModule

imported by: _pickle • pickle

_contextvars (builtin module)

imported by: _py_warnings • contextvars • threading

_csv (builtin module)

imported by: csv

_ctypes C:\Users\danil\AppData\Local\Programs\Python\Python314\DLLs\_ctypes.pyd

imports: ctypes._layout

imported by: ctypes • ctypes._layout • ctypes.macholib.dyld • numpy._core._dtype_ctypes

_datetime (builtin module)

imports: _strptime • time

imported by: datetime

_decimal C:\Users\danil\AppData\Local\Programs\Python\Python314\DLLs\_decimal.pyd

imported by: decimal

_dummy_thread MissingModule

imported by: numpy._core.arrayprint

_elementtree C:\Users\danil\AppData\Local\Programs\Python\Python314\DLLs\_elementtree.pyd

imports: pyexpat • xml.etree.ElementInclude • xml.etree.ElementPath • xml.etree.ElementTree • xml.etree.cElementTree

imported by: xml.etree.ElementTree

_frozen_importlib ExcludedModule

imported by: importlib • importlib.abc • zipimport

_frozen_importlib_external MissingModule

imported by: importlib • importlib._bootstrap • importlib.abc • zipimport

_functools (builtin module)

imported by: functools

_hashlib C:\Users\danil\AppData\Local\Programs\Python\Python314\DLLs\_hashlib.pyd

imported by: hashlib • hmac

_heapq (builtin module)

imported by: heapq

_hmac (builtin module)

imported by: hmac

_imp (builtin module)

imported by: importlib • importlib._bootstrap_external • importlib.util • zipimport

_interpqueues (builtin module)

imported by: concurrent.interpreters._queues

_interpreters (builtin module)

imported by: concurrent.futures • concurrent.interpreters

_io (builtin module)

imported by: importlib._bootstrap_external • io • zipimport

_ios_support SourceModule

imports: ctypes • ctypes.util • sys

imported by: webbrowser

_json (builtin module)

imports: json.decoder

imported by: json.decoder • json.encoder • json.scanner

_locale (builtin module)

imported by: locale

_lsprof (builtin module)

imported by: cProfile

_lzma C:\Users\danil\AppData\Local\Programs\Python\Python314\DLLs\_lzma.pyd

imported by: lzma

_md5 (builtin module)

imported by: hashlib

_multibytecodec (builtin module)

imported by: encodings.big5 • encodings.big5hkscs • encodings.cp932 • encodings.cp949 • encodings.cp950 • encodings.euc_jis_2004 • encodings.euc_jisx0213 • encodings.euc_jp • encodings.euc_kr • encodings.gb18030 • encodings.gb2312 • encodings.gbk • encodings.hz • encodings.iso2022_jp • encodings.iso2022_jp_1 • encodings.iso2022_jp_2 • encodings.iso2022_jp_2004 • encodings.iso2022_jp_3 • encodings.iso2022_jp_ext • encodings.iso2022_kr • encodings.johab • encodings.shift_jis • encodings.shift_jis_2004 • encodings.shift_jisx0213

_multiprocessing C:\Users\danil\AppData\Local\Programs\Python\Python314\DLLs\_multiprocessing.pyd

imported by: multiprocessing.connection • multiprocessing.resource_tracker • multiprocessing.synchronize

_opcode (builtin module)

imported by: dis • opcode

_opcode_metadata SourceModule

imported by: opcode

_operator (builtin module)

imported by: hmac • operator

_overlapped C:\Users\danil\AppData\Local\Programs\Python\Python314\DLLs\_overlapped.pyd

imported by: asyncio.windows_events

_pickle (builtin module)

imports: _compat_pickle • codecs • copyreg

imported by: pickle

_posixshmem MissingModule

imported by: multiprocessing.resource_tracker • multiprocessing.shared_memory

_posixsubprocess MissingModule

imports: gc

imported by: multiprocessing.util • subprocess

_py_abc SourceModule

imports: _weakrefset

imported by: abc

_py_warnings SourceModule

imports: _contextvars • _thread • builtins • functools • inspect • linecache • re • sys • traceback • tracemalloc • types

imported by: warnings

_pydatetime SourceModule

imports: _strptime • math • operator • sys • time • warnings

imported by: datetime

_pydecimal SourceModule

imports: collections • contextvars • itertools • locale • math • numbers • re • sys

imported by: decimal

_pyi_rth_utils Package

imports: _pyi_rth_utils.qt • os • sys

imported by: _pyi_rth_utils.qt • pyi_rth_pyqt6.py

_pyi_rth_utils.qt SourceModule

imports: _pyi_rth_utils • atexit • importlib • os

imported by: _pyi_rth_utils • pyi_rth_pyqt6.py

_pyrepl Package

imported by: _pyrepl.pager • _pyrepl.trace • _pyrepl.types • _pyrepl.utils

_pyrepl.pager SourceModule

imports: __future__ • _pyrepl • io • os • re • subprocess • sys • tempfile • termios • tty • typing

imported by: pydoc

_pyrepl.trace SourceModule

imports: __future__ • _pyrepl • os • posix • sys • typing

imported by: _pyrepl.utils

_pyrepl.types SourceModule

imports: 'collections.abc' • _pyrepl

imported by: _pyrepl.utils

_pyrepl.utils SourceModule

imports: __future__ • _colorize • _pyrepl • _pyrepl.trace • _pyrepl.types • builtins • collections • functools • io • keyword • re • token • tokenize • typing • unicodedata

imported by: pdb

_queue C:\Users\danil\AppData\Local\Programs\Python\Python314\DLLs\_queue.pyd

imported by: queue

_random (builtin module)

imported by: random

_scproxy MissingModule

imported by: urllib.request

_sha1 (builtin module)

imported by: hashlib

_sha2 (builtin module)

imported by: hashlib • random

_sha3 (builtin module)

imported by: hashlib

_signal (builtin module)

imported by: signal

_socket C:\Users\danil\AppData\Local\Programs\Python\Python314\DLLs\_socket.pyd

imported by: socket

_sre (builtin module)

imports: copy • re

imported by: re • re._compiler • re._constants

_ssl C:\Users\danil\AppData\Local\Programs\Python\Python314\DLLs\_ssl.pyd

imports: socket

imported by: ssl

_stat (builtin module)

imported by: stat

_statistics (builtin module)

imported by: statistics

_string (builtin module)

imported by: string

_strptime SourceModule

imports: _thread • calendar • datetime • locale • os • re • time • warnings

imported by: _datetime • _pydatetime • time

_struct (builtin module)

imported by: struct

_suggestions (builtin module)

imported by: traceback

_sysconfig (builtin module)

imported by: sysconfig

_thread (builtin module)

imported by: _py_warnings • _strptime • functools • numpy._core.arrayprint • reprlib • tempfile • threading

_threading_local SourceModule

imports: contextlib • threading • weakref

imported by: threading

_tokenize (builtin module)

imported by: tokenize

_tracemalloc (builtin module)

imported by: tracemalloc

_types (builtin module)

imported by: types

_typeshed MissingModule

imported by: numpy.random.bit_generator • scipy._lib.array_api_compat.common._typing

_typing (builtin module)

imported by: typing

_warnings (builtin module)

imported by: importlib._bootstrap_external • warnings

_weakref (builtin module)

imported by: _weakrefset • collections • weakref • xml.sax.expatreader

_weakrefset SourceModule

imports: _weakref • types

imported by: _py_abc • main.py • multiprocessing.process • threading • weakref

_winapi (builtin module)

imported by: asyncio.windows_events • asyncio.windows_utils • mimetypes • multiprocessing.connection • multiprocessing.heap • multiprocessing.popen_spawn_win32 • multiprocessing.reduction • multiprocessing.shared_memory • multiprocessing.spawn • ntpath • pathlib._os • shutil • subprocess • sysconfig

_wmi C:\Users\danil\AppData\Local\Programs\Python\Python314\DLLs\_wmi.pyd

imported by: platform

_zstd C:\Users\danil\AppData\Local\Programs\Python\Python314\DLLs\_zstd.pyd

imported by: compression.zstd • compression.zstd._zstdfile

abc SourceModule

imports: _abc • _py_abc

imported by: _collections_abc • contextlib • dataclasses • email._policybase • functools • importlib._abc • importlib.abc • importlib.metadata • importlib.resources.abc • inspect • io • main.py • multiprocessing.reduction • numbers • numpy.f2py._backends._backend • numpy.polynomial._polybase • numpy.random.bit_generator • os • scipy._lib._sparse • scipy.optimize._shgo_lib._vertex • scipy.stats._distribution_infrastructure • scipy.stats._probability_distribution • scipy.stats._qmc • selectors • typing

annotationlib SourceModule

imports: ast • builtins • enum • keyword • sys • types • typing • warnings

imported by: _collections_abc • dataclasses • functools • inspect • pydoc • scipy._lib._util • typing

argparse SourceModule

imports: _colorize • copy • difflib • gettext • os • re • shutil • sys • textwrap • warnings

imported by: ast • calendar • code • dis • doctest • gzip • http.server • inspect • mimetypes • numpy.f2py.f2py2e • pdb • platform • py_compile • random • serial.tools.list_ports • tarfile • tokenize • unittest.main • webbrowser • zipfile

array (builtin module)

imported by: multiprocessing.dummy • multiprocessing.managers • multiprocessing.reduction • serial.serialposix • serial.serialutil • socket

array_api_compat MissingModule

imported by: scipy._lib.array_api_extra._lib._utils._compat

ast SourceModule

imports: _ast • _ast_unparse • argparse • collections • inspect • re • sys

imported by: _ast_unparse • annotationlib • inspect • numpy._core._internal • numpy.lib._format_impl • numpy.lib._utils_impl • numpy.matrixlib.defmatrix • pydoc • traceback

asyncio Package

imports: asyncio • asyncio.base_events • asyncio.base_futures • asyncio.base_subprocess • asyncio.base_tasks • asyncio.constants • asyncio.coroutines • asyncio.events • asyncio.exceptions • asyncio.format_helpers • asyncio.futures • asyncio.graph • asyncio.locks • asyncio.mixins • asyncio.proactor_events • asyncio.protocols • asyncio.queues • asyncio.runners • asyncio.selector_events • asyncio.sslproto • asyncio.staggered • asyncio.streams • asyncio.subprocess • asyncio.taskgroups • asyncio.tasks • asyncio.threads • asyncio.timeouts • asyncio.transports • asyncio.trsock • asyncio.unix_events • asyncio.windows_events • asyncio.windows_utils • sys • warnings

imported by: asyncio • asyncio.base_events • asyncio.base_futures • asyncio.base_subprocess • asyncio.base_tasks • asyncio.constants • asyncio.coroutines • asyncio.events • asyncio.exceptions • asyncio.format_helpers • asyncio.futures • asyncio.graph • asyncio.locks • asyncio.log • asyncio.mixins • asyncio.proactor_events • asyncio.protocols • asyncio.queues • asyncio.runners • asyncio.selector_events • asyncio.sslproto • asyncio.staggered • asyncio.streams • asyncio.subprocess • asyncio.taskgroups • asyncio.tasks • asyncio.threads • asyncio.timeouts • asyncio.transports • asyncio.trsock • asyncio.unix_events • asyncio.windows_events • asyncio.windows_utils • pdb • unittest.async_case

asyncio.base_events SourceModule

imports: 'collections.abc' • asyncio • asyncio.constants • asyncio.coroutines • asyncio.events • asyncio.exceptions • asyncio.futures • asyncio.log • asyncio.protocols • asyncio.sslproto • asyncio.staggered • asyncio.tasks • asyncio.timeouts • asyncio.transports • asyncio.trsock • collections • concurrent.futures • errno • heapq • itertools • os • socket • ssl • stat • subprocess • sys • threading • time • traceback • warnings • weakref

imported by: asyncio • asyncio.proactor_events • asyncio.selector_events • asyncio.unix_events

asyncio.base_futures SourceModule

imports: asyncio • asyncio.format_helpers • reprlib

imported by: asyncio • asyncio.base_tasks • asyncio.futures

asyncio.base_subprocess SourceModule

imports: asyncio • asyncio.log • asyncio.protocols • asyncio.transports • collections • os • signal • subprocess • sys • warnings

imported by: asyncio • asyncio.unix_events • asyncio.windows_events

asyncio.base_tasks SourceModule

imports: asyncio • asyncio.base_futures • asyncio.coroutines • linecache • reprlib • traceback

imported by: asyncio • asyncio.tasks

asyncio.constants SourceModule

imports: asyncio • enum

imported by: asyncio • asyncio.base_events • asyncio.format_helpers • asyncio.proactor_events • asyncio.runners • asyncio.selector_events • asyncio.sslproto • asyncio.unix_events

asyncio.coroutines SourceModule

imports: 'collections.abc' • asyncio • inspect • os • sys • types • warnings

imported by: asyncio • asyncio.base_events • asyncio.base_tasks • asyncio.runners • asyncio.streams • asyncio.tasks • asyncio.unix_events

asyncio.events SourceModule

imports: _asyncio • asyncio • asyncio.format_helpers • asyncio.unix_events • asyncio.windows_events • contextvars • os • signal • socket • subprocess • sys • threading • warnings

imported by: asyncio • asyncio.base_events • asyncio.futures • asyncio.graph • asyncio.mixins • asyncio.runners • asyncio.selector_events • asyncio.staggered • asyncio.streams • asyncio.subprocess • asyncio.taskgroups • asyncio.tasks • asyncio.threads • asyncio.timeouts • asyncio.unix_events • asyncio.windows_events

asyncio.exceptions SourceModule

imports: asyncio

imported by: asyncio • asyncio.base_events • asyncio.futures • asyncio.locks • asyncio.proactor_events • asyncio.runners • asyncio.sslproto • asyncio.staggered • asyncio.streams • asyncio.taskgroups • asyncio.tasks • asyncio.timeouts • asyncio.unix_events • asyncio.windows_events

asyncio.format_helpers SourceModule

imports: asyncio • asyncio.constants • functools • inspect • reprlib • sys • traceback

imported by: asyncio • asyncio.base_futures • asyncio.events • asyncio.futures • asyncio.streams

asyncio.futures SourceModule

imports: _asyncio • asyncio • asyncio.base_futures • asyncio.events • asyncio.exceptions • asyncio.format_helpers • concurrent.futures • contextvars • logging • sys • types

imported by: asyncio • asyncio.base_events • asyncio.graph • asyncio.proactor_events • asyncio.selector_events • asyncio.staggered • asyncio.taskgroups • asyncio.tasks • asyncio.unix_events • asyncio.windows_events

asyncio.graph SourceModule

imports: asyncio • asyncio.events • asyncio.futures • asyncio.tasks • dataclasses • io • sys • types

imported by: asyncio

asyncio.locks SourceModule

imports: asyncio • asyncio.exceptions • asyncio.mixins • collections • enum

imported by: asyncio • asyncio.queues • asyncio.staggered

asyncio.log SourceModule

imports: asyncio • logging

imported by: asyncio.base_events • asyncio.base_subprocess • asyncio.proactor_events • asyncio.selector_events • asyncio.sslproto • asyncio.streams • asyncio.subprocess • asyncio.unix_events • asyncio.windows_events

asyncio.mixins SourceModule

imports: asyncio • asyncio.events • threading

imported by: asyncio • asyncio.locks • asyncio.queues

asyncio.proactor_events SourceModule

imports: asyncio • asyncio.base_events • asyncio.constants • asyncio.exceptions • asyncio.futures • asyncio.log • asyncio.protocols • asyncio.sslproto • asyncio.transports • asyncio.trsock • collections • io • os • signal • socket • threading • warnings

imported by: asyncio • asyncio.windows_events

asyncio.protocols SourceModule

imports: asyncio

imported by: asyncio • asyncio.base_events • asyncio.base_subprocess • asyncio.proactor_events • asyncio.selector_events • asyncio.sslproto • asyncio.streams • asyncio.subprocess

asyncio.queues SourceModule

imports: asyncio • asyncio.locks • asyncio.mixins • collections • heapq • types

imported by: asyncio • asyncio.tasks

asyncio.runners SourceModule

imports: asyncio • asyncio.constants • asyncio.coroutines • asyncio.events • asyncio.exceptions • asyncio.tasks • contextvars • enum • functools • inspect • signal • threading

imported by: asyncio

asyncio.selector_events SourceModule

imports: asyncio • asyncio.base_events • asyncio.constants • asyncio.events • asyncio.futures • asyncio.log • asyncio.protocols • asyncio.sslproto • asyncio.transports • asyncio.trsock • collections • errno • functools • itertools • os • selectors • socket • ssl • warnings • weakref

imported by: asyncio • asyncio.unix_events • asyncio.windows_events

asyncio.sslproto SourceModule

imports: asyncio • asyncio.constants • asyncio.exceptions • asyncio.log • asyncio.protocols • asyncio.transports • collections • enum • ssl • warnings

imported by: asyncio • asyncio.base_events • asyncio.proactor_events • asyncio.selector_events

asyncio.staggered SourceModule

imports: asyncio • asyncio.events • asyncio.exceptions • asyncio.futures • asyncio.locks • asyncio.tasks • contextlib

imported by: asyncio • asyncio.base_events

asyncio.streams SourceModule

imports: asyncio • asyncio.coroutines • asyncio.events • asyncio.exceptions • asyncio.format_helpers • asyncio.log • asyncio.protocols • asyncio.tasks • collections • socket • sys • warnings • weakref

imported by: asyncio • asyncio.subprocess

asyncio.subprocess SourceModule

imports: asyncio • asyncio.events • asyncio.log • asyncio.protocols • asyncio.streams • asyncio.tasks • subprocess

imported by: asyncio

asyncio.taskgroups SourceModule

imports: asyncio • asyncio.events • asyncio.exceptions • asyncio.futures • asyncio.tasks

imported by: asyncio

asyncio.tasks SourceModule

imports: _asyncio • asyncio • asyncio.base_tasks • asyncio.coroutines • asyncio.events • asyncio.exceptions • asyncio.futures • asyncio.queues • asyncio.timeouts • concurrent.futures • contextvars • functools • inspect • itertools • math • types • weakref

imported by: asyncio • asyncio.base_events • asyncio.graph • asyncio.runners • asyncio.staggered • asyncio.streams • asyncio.subprocess • asyncio.taskgroups • asyncio.timeouts • asyncio.unix_events • asyncio.windows_events

asyncio.threads SourceModule

imports: asyncio • asyncio.events • contextvars • functools

imported by: asyncio

asyncio.timeouts SourceModule

imports: asyncio • asyncio.events • asyncio.exceptions • asyncio.tasks • enum • types

imported by: asyncio • asyncio.base_events • asyncio.tasks

asyncio.transports SourceModule

imports: asyncio

imported by: asyncio • asyncio.base_events • asyncio.base_subprocess • asyncio.proactor_events • asyncio.selector_events • asyncio.sslproto • asyncio.unix_events

asyncio.trsock SourceModule

imports: asyncio • socket

imported by: asyncio • asyncio.base_events • asyncio.proactor_events • asyncio.selector_events

asyncio.unix_events SourceModule

imports: asyncio • asyncio.base_events • asyncio.base_subprocess • asyncio.constants • asyncio.coroutines • asyncio.events • asyncio.exceptions • asyncio.futures • asyncio.log • asyncio.selector_events • asyncio.tasks • asyncio.transports • errno • io • itertools • os • selectors • signal • socket • stat • subprocess • sys • threading • warnings

imported by: asyncio • asyncio.events

asyncio.windows_events SourceModule

imports: _overlapped • _winapi • asyncio • asyncio.base_subprocess • asyncio.events • asyncio.exceptions • asyncio.futures • asyncio.log • asyncio.proactor_events • asyncio.selector_events • asyncio.tasks • asyncio.windows_utils • errno • functools • math • msvcrt • socket • struct • sys • time • weakref

imported by: asyncio • asyncio.events

asyncio.windows_utils SourceModule

imports: _winapi • asyncio • itertools • msvcrt • os • subprocess • sys • tempfile • warnings

imported by: asyncio • asyncio.windows_events

atexit (builtin module)

imported by: _pyi_rth_utils.qt • colorama.initialise • logging • multiprocessing.forkserver • multiprocessing.popen_fork • multiprocessing.util • pdb • pyqtgraph • pyqtgraph.multiprocess.processes • pyqtgraph.widgets.RemoteGraphicsView • rlcompleter • weakref

base64 SourceModule

imports: binascii • getopt • struct • sys

imported by: email._encoded_words • email.base64mime • email.encoders • encodings.base64_codec • http.server • secrets • shiboken6 • ssl • urllib.request • xmlrpc.client

bdb SourceModule

imports: contextlib • dis • fnmatch • functools • inspect • linecache • os • reprlib • sys • threading • weakref

imported by: pdb

binascii (builtin module)

imported by: base64 • email._encoded_words • email.base64mime • email.contentmanager • email.header • email.message • encodings.hex_codec • encodings.uu_codec • http.server • quopri • zipfile

bisect SourceModule

imports: _bisect

imported by: multiprocessing.heap • pyqtgraph.graphicsItems.PlotDataItem • random • scipy.sparse._lil • statistics • urllib.request

bottleneck MissingModule

imported by: pyqtgraph.imageview.ImageView

builtins (builtin module)

imported by: _py_warnings • _pyrepl.utils • annotationlib • bz2 • code • codecs • doctest • enum • gettext • gzip • inspect • locale • lzma • numpy._core.numeric • numpy._core.numerictypes • numpy.lib._function_base_impl • numpy.ma.core • numpy.random.mtrand • opcode • operator • pdb • pydoc • pyqtgraph.multiprocess.remoteproxy • pyqtgraph.parametertree.parameterTypes.basetypes • reprlib • rlcompleter • scipy._lib.array_api_compat.cupy._aliases • scipy._lib.array_api_compat.dask.array._aliases • scipy._lib.array_api_compat.numpy._aliases • scipy._lib.array_api_compat.torch._aliases • scipy.signal._filter_design • scipy.stats._binned_statistic • subprocess • tarfile • tokenize

bz2 SourceModule

imports: _bz2 • builtins • compression._common • compression._common._streams • io • os

imported by: encodings.bz2_codec • fileinput • numpy.lib._datasource • shutil • tarfile • zipfile

cProfile SourceModule

imports: _lsprof • importlib.machinery • importlib.util • io • marshal • optparse • os • profile • pstats • runpy • sys

imported by: pyqtgraph.debug

calendar SourceModule

imports: _colorize • argparse • datetime • enum • itertools • locale • sys • warnings

imported by: _strptime • email._parseaddr • http.cookiejar • ssl

cffi MissingModule

imported by: scipy._lib._ccallback

charset_normalizer MissingModule

imported by: numpy.f2py.crackfortran

cmath (builtin module)

imported by: scipy.signal._czt • scipy.signal._filter_design

cmd SourceModule

imports: inspect • readline • sys

imported by: pdb • pstats

code SourceModule

imports: argparse • builtins • codeop • readline • sys • traceback

imported by: pdb • pyqtgraph.console.repl_widget

codecs SourceModule

imports: _codecs • builtins • encodings • sys • warnings

imported by: _pickle • encodings • encodings._win_cp_codecs • encodings.ascii • encodings.base64_codec • encodings.big5 • encodings.big5hkscs • encodings.bz2_codec • encodings.charmap • encodings.cp037 • encodings.cp1006 • encodings.cp1026 • encodings.cp1125 • encodings.cp1140 • encodings.cp1250 • encodings.cp1251 • encodings.cp1252 • encodings.cp1253 • encodings.cp1254 • encodings.cp1255 • encodings.cp1256 • encodings.cp1257 • encodings.cp1258 • encodings.cp273 • encodings.cp424 • encodings.cp437 • encodings.cp500 • encodings.cp720 • encodings.cp737 • encodings.cp775 • encodings.cp850 • encodings.cp852 • encodings.cp855 • encodings.cp856 • encodings.cp857 • encodings.cp858 • encodings.cp860 • encodings.cp861 • encodings.cp862 • encodings.cp863 • encodings.cp864 • encodings.cp865 • encodings.cp866 • encodings.cp869 • encodings.cp874 • encodings.cp875 • encodings.cp932 • encodings.cp949 • encodings.cp950 • encodings.euc_jis_2004 • encodings.euc_jisx0213 • encodings.euc_jp • encodings.euc_kr • encodings.gb18030 • encodings.gb2312 • encodings.gbk • encodings.hex_codec • encodings.hp_roman8 • encodings.hz • encodings.idna • encodings.iso2022_jp • encodings.iso2022_jp_1 • encodings.iso2022_jp_2 • encodings.iso2022_jp_2004 • encodings.iso2022_jp_3 • encodings.iso2022_jp_ext • encodings.iso2022_kr • encodings.iso8859_1 • encodings.iso8859_10 • encodings.iso8859_11 • encodings.iso8859_13 • encodings.iso8859_14 • encodings.iso8859_15 • encodings.iso8859_16 • encodings.iso8859_2 • encodings.iso8859_3 • encodings.iso8859_4 • encodings.iso8859_5 • encodings.iso8859_6 • encodings.iso8859_7 • encodings.iso8859_8 • encodings.iso8859_9 • encodings.johab • encodings.koi8_r • encodings.koi8_t • encodings.koi8_u • encodings.kz1048 • encodings.latin_1 • encodings.mac_arabic • encodings.mac_croatian • encodings.mac_cyrillic • encodings.mac_farsi • encodings.mac_greek • encodings.mac_iceland • encodings.mac_latin2 • encodings.mac_roman • encodings.mac_romanian • encodings.mac_turkish • encodings.mbcs • encodings.oem • encodings.palmos • encodings.ptcp154 • encodings.punycode • encodings.quopri_codec • encodings.raw_unicode_escape • encodings.rot_13 • encodings.shift_jis • encodings.shift_jis_2004 • encodings.shift_jisx0213 • encodings.tis_620 • encodings.undefined • encodings.unicode_escape • encodings.utf_16 • encodings.utf_16_be • encodings.utf_16_le • encodings.utf_32 • encodings.utf_32_be • encodings.utf_32_le • encodings.utf_7 • encodings.utf_8 • encodings.utf_8_sig • encodings.uu_codec • encodings.zlib_codec • json • main.py • numpy.f2py.crackfortran • pickle • tokenize • xml.sax.saxutils

codeop SourceModule

imports: __future__ • warnings

imported by: code • pdb • traceback

collections Package

imports: _collections • _collections_abc • _weakref • copy • heapq • itertools • keyword • operator • reprlib • sys

imported by: PyQt6.QtCore • PyQt6.QtGui • PyQt6.QtOpenGL • PyQt6.QtOpenGLWidgets • PyQt6.QtSvg • PyQt6.QtTest • PyQt6.QtWidgets • _pydecimal • _pyrepl.utils • ast • asyncio.base_events • asyncio.base_subprocess • asyncio.locks • asyncio.proactor_events • asyncio.queues • asyncio.selector_events • asyncio.sslproto • asyncio.streams • concurrent.futures._base • contextlib • difflib • dis • doctest • email.feedparser • functools • importlib.metadata • importlib.metadata._collections • importlib.resources.readers • inspect • main.py • modules.processor • multiprocessing.heap • multiprocessing.pool • multiprocessing.queues • numpy._core.overrides • numpy._core.records • pkgutil • platform • pprint • pydoc • pyqtgraph.configfile • pyqtgraph.flowchart.Flowchart • pyqtgraph.flowchart.Node • pyqtgraph.flowchart.NodeLibrary • pyqtgraph.functions • pyqtgraph.graphicsItems.DateAxisItem • pyqtgraph.graphicsItems.GraphicsItem • pyqtgraph.graphicsItems.ScatterPlotItem • pyqtgraph.parametertree.Parameter • pyqtgraph.parametertree.SystemSolver • pyqtgraph.parametertree.parameterTypes.list • pyqtgraph.widgets.ColorMapMenu • pyqtgraph.widgets.ColorMapWidget • pyqtgraph.widgets.ComboBox • pyqtgraph.widgets.DataFilterWidget • pyqtgraph.widgets.DataTreeWidget • pyqtgraph.widgets.ScatterPlotWidget • queue • scipy._lib._docscrape • scipy._lib._pep440 • scipy._lib._util • scipy.integrate._quad_vec • scipy.integrate._quadrature • scipy.optimize._differentiable_functions • scipy.optimize._linprog_util • scipy.optimize._shgo • scipy.optimize._shgo_lib._vertex • scipy.optimize._spectral • scipy.optimize._zeros_py • scipy.special._basic • scipy.special._multiufuncs • scipy.stats._binned_statistic • scipy.stats._common • scipy.stats._fit • scipy.stats._hypotests • scipy.stats._mannwhitneyu • scipy.stats._morestats • scipy.stats._mstats_basic • scipy.stats._stats_py • selectors • shlex • shutil • ssl • statistics • string • threading • tokenize • typing • unittest._log • unittest.case • unittest.util • urllib.parse • xml.etree.ElementTree

colorama Package

imports: colorama • colorama.ansi • colorama.ansitowin32 • colorama.initialise • colorama.win32

imported by: colorama • colorama.ansi • colorama.ansitowin32 • colorama.initialise • colorama.win32 • colorama.winterm

colorama.ansi SourceModule

imports: colorama

imported by: colorama • colorama.ansitowin32

colorama.ansitowin32 SourceModule

imports: colorama • colorama.ansi • colorama.win32 • colorama.winterm • os • re • sys

imported by: colorama • colorama.initialise

colorama.initialise SourceModule

imports: atexit • colorama • colorama.ansitowin32 • contextlib • sys

imported by: colorama

colorama.win32 SourceModule

imports: colorama • ctypes • ctypes.wintypes

imported by: colorama • colorama.ansitowin32 • colorama.winterm • pyqtgraph.util.cprint

colorama.winterm SourceModule

imports: colorama • colorama.win32 • msvcrt

imported by: colorama.ansitowin32 • pyqtgraph.util.cprint

colorcet MissingModule

imported by: pyqtgraph.colormap • pyqtgraph.widgets.ColorMapMenu

compression Package

imports: compression.zstd

imported by: compression._common • compression.zstd • shutil • tarfile • zipfile

compression._common Package

imports: compression • compression._common._streams

imported by: bz2 • compression._common._streams • compression.zstd._zstdfile • gzip • lzma

compression._common._streams SourceModule

imports: compression._common • io • sys

imported by: bz2 • compression._common • compression.zstd._zstdfile • gzip • lzma

compression.zstd Package

imports: _zstd • compression • compression.zstd._zstdfile • enum

imported by: compression • compression.zstd._zstdfile • shutil • tarfile • zipfile

compression.zstd._zstdfile SourceModule

imports: _zstd • compression._common • compression._common._streams • compression.zstd • io • os

imported by: compression.zstd

concurrent Package

imports: concurrent.interpreters

imported by: concurrent.futures • concurrent.futures.interpreter • concurrent.interpreters

concurrent.futures Package

imports: _interpreters • concurrent • concurrent.futures • concurrent.futures._base • concurrent.futures.interpreter • concurrent.futures.process • concurrent.futures.thread

imported by: PyQt6.uic.compile_ui • asyncio.base_events • asyncio.futures • asyncio.tasks • concurrent.futures • concurrent.futures._base • concurrent.futures.interpreter • concurrent.futures.process • concurrent.futures.thread • numpy.testing._private.utils

concurrent.futures._base SourceModule

imports: collections • concurrent.futures • itertools • logging • threading • time • types • weakref

imported by: concurrent.futures • concurrent.futures.process • concurrent.futures.thread

concurrent.futures.interpreter SourceModule

imports: concurrent • concurrent.futures • concurrent.futures.thread • concurrent.interpreters • sys • textwrap • traceback

imported by: concurrent.futures

concurrent.futures.process SourceModule

imports: concurrent.futures • concurrent.futures._base • functools • itertools • multiprocessing • multiprocessing.connection • multiprocessing.queues • multiprocessing.synchronize • os • queue • sys • threading • traceback • weakref

imported by: concurrent.futures

concurrent.futures.thread SourceModule

imports: concurrent.futures • concurrent.futures._base • itertools • os • queue • threading • types • weakref

imported by: concurrent.futures • concurrent.futures.interpreter

concurrent.interpreters Package

imports: _interpreters • concurrent • concurrent.interpreters • concurrent.interpreters._crossinterp • concurrent.interpreters._queues • threading • weakref

imported by: concurrent • concurrent.futures.interpreter • concurrent.interpreters • concurrent.interpreters._crossinterp • concurrent.interpreters._queues

concurrent.interpreters._crossinterp SourceModule

imports: concurrent.interpreters

imported by: concurrent.interpreters • concurrent.interpreters._queues

concurrent.interpreters._queues SourceModule

imports: _interpqueues • concurrent.interpreters • concurrent.interpreters._crossinterp • pickle • queue • time • weakref

imported by: concurrent.interpreters

contextlib SourceModule

imports: _collections_abc • abc • collections • functools • os • sys • types

imported by: _aix_support • _ast_unparse • _threading_local • asyncio.staggered • bdb • colorama.initialise • glob • http.server • importlib.metadata • importlib.resources._adapters • importlib.resources._common • importlib.resources.readers • numpy._core._methods • numpy._core.arrayprint • numpy._core.memmap • numpy._core.records • numpy.lib._histograms_impl • numpy.lib._npyio_impl • numpy.testing._private.utils • pdb • pyqtgraph.Qt • pyqtgraph.configfile • pyqtgraph.debug • pyqtgraph.exporters.SVGExporter • pyqtgraph.parametertree.interactive • pyqtgraph.parametertree.parameterTypes.pen • pyqtgraph.widgets.BusyCursor • scipy._lib._array_api • scipy._lib._uarray._backend • scipy._lib._util • scipy._lib.array_api_extra.testing • scipy._lib.cobyqa.problem • scipy.fft._pocketfft.helper • shiboken6 • subprocess • traceback • typing • unittest.case • urllib.request • xml.etree.ElementTree • zipfile._path

contextvars SourceModule

imports: _collections_abc • _contextvars

imported by: _pydecimal • asyncio.events • asyncio.futures • asyncio.runners • asyncio.tasks • asyncio.threads • numpy._core.printoptions • scipy._lib._array_api • unittest.async_case

controller SourceModule

imports: PyQt6 • PyQt6.QtCore • PyQt6.QtWidgets • csv • json • logging • modules.data_viewer • modules.processor • modules.protocol_defs • modules.serial_manager • pyqtgraph • pyqtgraph.exporters • serial.tools.list_ports • time

imported by: main.py

copy SourceModule

imports: copyreg • types • weakref

imported by: _sre • argparse • collections • dataclasses • email.generator • gettext • http.cookiejar • http.server • numpy.f2py.capi_maps • numpy.f2py.cfuncs • numpy.f2py.crackfortran • numpy.f2py.func2subr • numpy.f2py.rules • numpy.ma.core • pyqtgraph.graphicsItems.ViewBox.ViewBox • pyqtgraph.parametertree.SystemSolver • scipy._lib._docscrape • scipy._lib.cobyqa.problem • scipy._lib.pyprima.cobyla.cobyla • scipy.integrate._odepack_py • scipy.integrate._quad_vec • scipy.optimize._linprog • scipy.optimize._shgo_lib._complex • scipy.signal._ltisys • scipy.sparse.linalg._dsolve.linsolve • scipy.stats._qmc • tarfile • weakref • webbrowser • xml.dom.xmlbuilder • xml.etree.ElementInclude

copyreg SourceModule

imports: operator • typing

imported by: _pickle • copy • main.py • multiprocessing.reduction • numpy._core • pickle • re • scipy._lib._uarray._backend • typing

csv SourceModule

imports: _csv • io • re • types

imported by: controller • importlib.metadata • modules.data_viewer • pyqtgraph.exporters.CSVExporter

ctypes Package

imports: _ctypes • ctypes._endian • ctypes.util • nt • os • struct • sys • types • warnings

imported by: _ios_support • colorama.win32 • ctypes._aix • ctypes._endian • ctypes._layout • ctypes.macholib • ctypes.util • ctypes.wintypes • main.py • multiprocessing.sharedctypes • numpy._core._dtype_ctypes • numpy._core._internal • numpy.ctypeslib._ctypeslib • platform • pyqtgraph.Qt • pyqtgraph.Qt.internals • scipy._lib._ccallback • scipy.stats._continuous_distns • serial.serialwin32 • serial.tools.list_ports_osx • serial.tools.list_ports_windows • serial.win32 • webbrowser

ctypes._aix SourceModule

imports: ctypes • os • re • subprocess • sys

imported by: ctypes.util

ctypes._endian SourceModule

imports: ctypes • sys

imported by: ctypes

ctypes._layout SourceModule

imports: _ctypes • ctypes • sys • warnings

imported by: _ctypes

ctypes.macholib Package

imports: ctypes

imported by: ctypes.macholib.dyld • ctypes.macholib.dylib • ctypes.macholib.framework

ctypes.macholib.dyld SourceModule

imports: _ctypes • ctypes.macholib • ctypes.macholib.dylib • ctypes.macholib.framework • itertools • os

imported by: ctypes.util

ctypes.macholib.dylib SourceModule

imports: ctypes.macholib • re

imported by: ctypes.macholib.dyld

ctypes.macholib.framework SourceModule

imports: ctypes.macholib • re

imported by: ctypes.macholib.dyld

ctypes.util SourceModule

imports: ctypes • ctypes._aix • ctypes.macholib.dyld • ctypes.wintypes • importlib.machinery • os • re • shutil • struct • subprocess • sys • tempfile

imported by: _ios_support • ctypes

ctypes.wintypes SourceModule

imports: ctypes

imported by: colorama.win32 • ctypes.util • serial.tools.list_ports_windows • serial.win32

cuda MissingModule

imported by: pyqtgraph.widgets.RawImageWidget

cupy MissingModule

imported by: pyqtgraph.util.cupy_helper • scipy._lib.array_api_compat.common._helpers • scipy._lib.array_api_compat.cupy • scipy._lib.array_api_compat.cupy._aliases • scipy._lib.array_api_compat.cupy._info • scipy._lib.array_api_compat.cupy._typing

cupyx MissingModule

imported by: scipy._lib._array_api

cython MissingModule

imported by: scipy._lib._testutils

dask MissingModule

imported by: scipy._lib.array_api_compat.common._helpers • scipy._lib.array_api_extra._lib._lazy • scipy._lib.array_api_extra.testing

dataclasses SourceModule

imports: abc • annotationlib • copy • inspect • itertools • keyword • re • reprlib • sys • types • typing

imported by: _colorize • asyncio.graph • pprint • pstats • scipy._lib._array_api • scipy._lib.pyprima.cobyla.cobyla • scipy.integrate._cubature • scipy.spatial.distance • scipy.special._support_alternative_backends • scipy.stats._hypotests • scipy.stats._multicomp • scipy.stats._page_trend_test • scipy.stats._relative_risk • scipy.stats._resampling • scipy.stats._sensitivity_analysis • scipy.stats._stats_py • scipy.stats._survival

datetime SourceModule

imports: _datetime • _pydatetime • time

imported by: PyQt6.QtCore • PyQt6.QtGui • PyQt6.QtOpenGL • PyQt6.QtOpenGLWidgets • PyQt6.QtSvg • PyQt6.QtTest • PyQt6.QtWidgets • _strptime • calendar • email.utils • http.cookiejar • http.server • pyqtgraph.configfile • pyqtgraph.graphicsItems.DateAxisItem • xmlrpc.client

decimal SourceModule

imports: _decimal • _pydecimal • sys

imported by: fractions • pyqtgraph.functions • pyqtgraph.widgets.SpinBox • scipy.optimize._shgo_lib._complex • statistics • xmlrpc.client

difflib SourceModule

imports: collections • heapq • re • types

imported by: argparse • doctest • numpy.testing._private.utils • scipy.optimize._nonlin • traceback • unittest.case

dis SourceModule

imports: _opcode • argparse • collections • io • opcode • sys • types

imported by: bdb • inspect • pdb

doctest SourceModule

imports: __future__ • _colorize • argparse • builtins • collections • difflib • inspect • io • linecache • os • pdb • re • sys • traceback • unittest

imported by: numpy.testing._private.utils

email Package

imports: email._header_value_parser • email.charset • email.errors • email.header • email.parser

imported by: email._encoded_words • email._header_value_parser • email._parseaddr • email._policybase • email.base64mime • email.charset • email.contentmanager • email.encoders • email.errors • email.feedparser • email.generator • email.header • email.headerregistry • email.iterators • email.message • email.parser • email.policy • email.quoprimime • email.utils • importlib.metadata • urllib.request

email._encoded_words SourceModule

imports: base64 • binascii • email • email.errors • functools • re • string

imported by: email._header_value_parser • email.message

email._header_value_parser SourceModule

imports: email • email._encoded_words • email.errors • email.utils • operator • re • string • sys • urllib

imported by: email • email.headerregistry

email._parseaddr SourceModule

imports: calendar • email • time

imported by: email.utils

email._policybase SourceModule

imports: abc • email • email.charset • email.header • email.utils • re

imported by: email.feedparser • email.message • email.parser • email.policy

email.base64mime SourceModule

imports: base64 • binascii • email

imported by: email.charset • email.header

email.charset SourceModule

imports: email • email.base64mime • email.encoders • email.errors • email.quoprimime • functools

imported by: email • email._policybase • email.contentmanager • email.header • email.message • email.utils

email.contentmanager SourceModule

imports: binascii • email • email.charset • email.errors • email.message • email.quoprimime

imported by: email.policy

email.encoders SourceModule

imports: base64 • email • quopri

imported by: email.charset

email.errors SourceModule

imports: email

imported by: email • email._encoded_words • email._header_value_parser • email.charset • email.contentmanager • email.feedparser • email.generator • email.header • email.headerregistry • email.message

email.feedparser SourceModule

imports: collections • email • email._policybase • email.errors • email.message • io • re

imported by: email.parser

email.generator SourceModule

imports: copy • email • email.errors • email.utils • io • random • re • sys • time

imported by: email.message

email.header SourceModule

imports: binascii • email • email.base64mime • email.charset • email.errors • email.quoprimime • re

imported by: email • email._policybase

email.headerregistry SourceModule

imports: email • email._header_value_parser • email.errors • email.utils • types

imported by: email.policy

email.iterators SourceModule

imports: email • io • sys

imported by: email.message

email.message SourceModule

imports: binascii • email • email._encoded_words • email._policybase • email.charset • email.errors • email.generator • email.iterators • email.policy • email.utils • io • quopri • re

imported by: email.contentmanager • email.feedparser • email.policy • http.client • importlib.metadata._adapters • pydoc

email.parser SourceModule

imports: email • email._policybase • email.feedparser • io

imported by: email • http.client

email.policy SourceModule

imports: email • email._policybase • email.contentmanager • email.headerregistry • email.message • email.utils • re • sys

imported by: email.message

email.quoprimime SourceModule

imports: email • re • string

imported by: email.charset • email.contentmanager • email.header

email.utils SourceModule

imports: datetime • email • email._parseaddr • email.charset • os • random • re • socket • time • urllib.parse

imported by: email._header_value_parser • email._policybase • email.generator • email.headerregistry • email.message • email.policy • http.server • urllib.request

encodings Package

imports: codecs • encodings • encodings._win_cp_codecs • encodings.aliases • encodings.ascii • encodings.base64_codec • encodings.big5 • encodings.big5hkscs • encodings.bz2_codec • encodings.charmap • encodings.cp037 • encodings.cp1006 • encodings.cp1026 • encodings.cp1125 • encodings.cp1140 • encodings.cp1250 • encodings.cp1251 • encodings.cp1252 • encodings.cp1253 • encodings.cp1254 • encodings.cp1255 • encodings.cp1256 • encodings.cp1257 • encodings.cp1258 • encodings.cp273 • encodings.cp424 • encodings.cp437 • encodings.cp500 • encodings.cp720 • encodings.cp737 • encodings.cp775 • encodings.cp850 • encodings.cp852 • encodings.cp855 • encodings.cp856 • encodings.cp857 • encodings.cp858 • encodings.cp860 • encodings.cp861 • encodings.cp862 • encodings.cp863 • encodings.cp864 • encodings.cp865 • encodings.cp866 • encodings.cp869 • encodings.cp874 • encodings.cp875 • encodings.cp932 • encodings.cp949 • encodings.cp950 • encodings.euc_jis_2004 • encodings.euc_jisx0213 • encodings.euc_jp • encodings.euc_kr • encodings.gb18030 • encodings.gb2312 • encodings.gbk • encodings.hex_codec • encodings.hp_roman8 • encodings.hz • encodings.idna • encodings.iso2022_jp • encodings.iso2022_jp_1 • encodings.iso2022_jp_2 • encodings.iso2022_jp_2004 • encodings.iso2022_jp_3 • encodings.iso2022_jp_ext • encodings.iso2022_kr • encodings.iso8859_1 • encodings.iso8859_10 • encodings.iso8859_11 • encodings.iso8859_13 • encodings.iso8859_14 • encodings.iso8859_15 • encodings.iso8859_16 • encodings.iso8859_2 • encodings.iso8859_3 • encodings.iso8859_4 • encodings.iso8859_5 • encodings.iso8859_6 • encodings.iso8859_7 • encodings.iso8859_8 • encodings.iso8859_9 • encodings.johab • encodings.koi8_r • encodings.koi8_t • encodings.koi8_u • encodings.kz1048 • encodings.latin_1 • encodings.mac_arabic • encodings.mac_croatian • encodings.mac_cyrillic • encodings.mac_farsi • encodings.mac_greek • encodings.mac_iceland • encodings.mac_latin2 • encodings.mac_roman • encodings.mac_romanian • encodings.mac_turkish • encodings.mbcs • encodings.oem • encodings.palmos • encodings.ptcp154 • encodings.punycode • encodings.quopri_codec • encodings.raw_unicode_escape • encodings.rot_13 • encodings.shift_jis • encodings.shift_jis_2004 • encodings.shift_jisx0213 • encodings.tis_620 • encodings.undefined • encodings.unicode_escape • encodings.utf_16 • encodings.utf_16_be • encodings.utf_16_le • encodings.utf_32 • encodings.utf_32_be • encodings.utf_32_le • encodings.utf_7 • encodings.utf_8 • encodings.utf_8_sig • encodings.uu_codec • encodings.zlib_codec • sys

imported by: codecs • encodings • encodings._win_cp_codecs • encodings.aliases • encodings.ascii • encodings.base64_codec • encodings.big5 • encodings.big5hkscs • encodings.bz2_codec • encodings.charmap • encodings.cp037 • encodings.cp1006 • encodings.cp1026 • encodings.cp1125 • encodings.cp1140 • encodings.cp1250 • encodings.cp1251 • encodings.cp1252 • encodings.cp1253 • encodings.cp1254 • encodings.cp1255 • encodings.cp1256 • encodings.cp1257 • encodings.cp1258 • encodings.cp273 • encodings.cp424 • encodings.cp437 • encodings.cp500 • encodings.cp720 • encodings.cp737 • encodings.cp775 • encodings.cp850 • encodings.cp852 • encodings.cp855 • encodings.cp856 • encodings.cp857 • encodings.cp858 • encodings.cp860 • encodings.cp861 • encodings.cp862 • encodings.cp863 • encodings.cp864 • encodings.cp865 • encodings.cp866 • encodings.cp869 • encodings.cp874 • encodings.cp875 • encodings.cp932 • encodings.cp949 • encodings.cp950 • encodings.euc_jis_2004 • encodings.euc_jisx0213 • encodings.euc_jp • encodings.euc_kr • encodings.gb18030 • encodings.gb2312 • encodings.gbk • encodings.hex_codec • encodings.hp_roman8 • encodings.hz • encodings.idna • encodings.iso2022_jp • encodings.iso2022_jp_1 • encodings.iso2022_jp_2 • encodings.iso2022_jp_2004 • encodings.iso2022_jp_3 • encodings.iso2022_jp_ext • encodings.iso2022_kr • encodings.iso8859_1 • encodings.iso8859_10 • encodings.iso8859_11 • encodings.iso8859_13 • encodings.iso8859_14 • encodings.iso8859_15 • encodings.iso8859_16 • encodings.iso8859_2 • encodings.iso8859_3 • encodings.iso8859_4 • encodings.iso8859_5 • encodings.iso8859_6 • encodings.iso8859_7 • encodings.iso8859_8 • encodings.iso8859_9 • encodings.johab • encodings.koi8_r • encodings.koi8_t • encodings.koi8_u • encodings.kz1048 • encodings.latin_1 • encodings.mac_arabic • encodings.mac_croatian • encodings.mac_cyrillic • encodings.mac_farsi • encodings.mac_greek • encodings.mac_iceland • encodings.mac_latin2 • encodings.mac_roman • encodings.mac_romanian • encodings.mac_turkish • encodings.mbcs • encodings.oem • encodings.palmos • encodings.ptcp154 • encodings.punycode • encodings.quopri_codec • encodings.raw_unicode_escape • encodings.rot_13 • encodings.shift_jis • encodings.shift_jis_2004 • encodings.shift_jisx0213 • encodings.tis_620 • encodings.undefined • encodings.unicode_escape • encodings.utf_16 • encodings.utf_16_be • encodings.utf_16_le • encodings.utf_32 • encodings.utf_32_be • encodings.utf_32_le • encodings.utf_7 • encodings.utf_8 • encodings.utf_8_sig • encodings.uu_codec • encodings.zlib_codec • locale • main.py

encodings._win_cp_codecs SourceModule

imports: codecs • encodings

imported by: encodings • main.py

encodings.aliases SourceModule

imports: encodings

imported by: encodings • locale • main.py

encodings.ascii SourceModule

imports: codecs • encodings

imported by: encodings • main.py

encodings.base64_codec SourceModule

imports: base64 • codecs • encodings

imported by: encodings • main.py

encodings.big5 SourceModule

imports: _codecs_tw • _multibytecodec • codecs • encodings

imported by: encodings • main.py

encodings.big5hkscs SourceModule

imports: _codecs_hk • _multibytecodec • codecs • encodings

imported by: encodings • main.py

encodings.bz2_codec SourceModule

imports: bz2 • codecs • encodings

imported by: encodings • main.py

encodings.charmap SourceModule

imports: codecs • encodings

imported by: encodings • main.py

encodings.cp037 SourceModule

imports: codecs • encodings

imported by: encodings • main.py

encodings.cp1006 SourceModule

imports: codecs • encodings

imported by: encodings • main.py

encodings.cp1026 SourceModule

imports: codecs • encodings

imported by: encodings • main.py

encodings.cp1125 SourceModule

imports: codecs • encodings

imported by: encodings • main.py

encodings.cp1140 SourceModule

imports: codecs • encodings

imported by: encodings • main.py

encodings.cp1250 SourceModule

imports: codecs • encodings

imported by: encodings • main.py

encodings.cp1251 SourceModule

imports: codecs • encodings

imported by: encodings • main.py

encodings.cp1252 SourceModule

imports: codecs • encodings

imported by: encodings • main.py

encodings.cp1253 SourceModule

imports: codecs • encodings

imported by: encodings • main.py

encodings.cp1254 SourceModule

imports: codecs • encodings

imported by: encodings • main.py

encodings.cp1255 SourceModule

imports: codecs • encodings

imported by: encodings • main.py

encodings.cp1256 SourceModule

imports: codecs • encodings

imported by: encodings • main.py

encodings.cp1257 SourceModule

imports: codecs • encodings

imported by: encodings • main.py

encodings.cp1258 SourceModule

imports: codecs • encodings

imported by: encodings • main.py

encodings.cp273 SourceModule

imports: codecs • encodings

imported by: encodings • main.py

encodings.cp424 SourceModule

imports: codecs • encodings

imported by: encodings • main.py

encodings.cp437 SourceModule

imports: codecs • encodings

imported by: encodings • main.py

encodings.cp500 SourceModule

imports: codecs • encodings

imported by: encodings • main.py

encodings.cp720 SourceModule

imports: codecs • encodings

imported by: encodings • main.py

encodings.cp737 SourceModule

imports: codecs • encodings

imported by: encodings • main.py

encodings.cp775 SourceModule

imports: codecs • encodings

imported by: encodings • main.py

encodings.cp850 SourceModule

imports: codecs • encodings

imported by: encodings • main.py

encodings.cp852 SourceModule

imports: codecs • encodings

imported by: encodings • main.py

encodings.cp855 SourceModule

imports: codecs • encodings

imported by: encodings • main.py

encodings.cp856 SourceModule

imports: codecs • encodings

imported by: encodings • main.py

encodings.cp857 SourceModule

imports: codecs • encodings

imported by: encodings • main.py

encodings.cp858 SourceModule

imports: codecs • encodings

imported by: encodings • main.py

encodings.cp860 SourceModule

imports: codecs • encodings

imported by: encodings • main.py

encodings.cp861 SourceModule

imports: codecs • encodings

imported by: encodings • main.py

encodings.cp862 SourceModule

imports: codecs • encodings

imported by: encodings • main.py

encodings.cp863 SourceModule

imports: codecs • encodings

imported by: encodings • main.py

encodings.cp864 SourceModule

imports: codecs • encodings

imported by: encodings • main.py

encodings.cp865 SourceModule

imports: codecs • encodings

imported by: encodings • main.py

encodings.cp866 SourceModule

imports: codecs • encodings

imported by: encodings • main.py

encodings.cp869 SourceModule

imports: codecs • encodings

imported by: encodings • main.py

encodings.cp874 SourceModule

imports: codecs • encodings

imported by: encodings • main.py

encodings.cp875 SourceModule

imports: codecs • encodings

imported by: encodings • main.py

encodings.cp932 SourceModule

imports: _codecs_jp • _multibytecodec • codecs • encodings

imported by: encodings • main.py

encodings.cp949 SourceModule

imports: _codecs_kr • _multibytecodec • codecs • encodings

imported by: encodings • main.py

encodings.cp950 SourceModule

imports: _codecs_tw • _multibytecodec • codecs • encodings

imported by: encodings • main.py

encodings.euc_jis_2004 SourceModule

imports: _codecs_jp • _multibytecodec • codecs • encodings

imported by: encodings • main.py

encodings.euc_jisx0213 SourceModule

imports: _codecs_jp • _multibytecodec • codecs • encodings

imported by: encodings • main.py

encodings.euc_jp SourceModule

imports: _codecs_jp • _multibytecodec • codecs • encodings

imported by: encodings • main.py

encodings.euc_kr SourceModule

imports: _codecs_kr • _multibytecodec • codecs • encodings

imported by: encodings • main.py

encodings.gb18030 SourceModule

imports: _codecs_cn • _multibytecodec • codecs • encodings

imported by: encodings • main.py

encodings.gb2312 SourceModule

imports: _codecs_cn • _multibytecodec • codecs • encodings

imported by: encodings • main.py

encodings.gbk SourceModule

imports: _codecs_cn • _multibytecodec • codecs • encodings

imported by: encodings • main.py

encodings.hex_codec SourceModule

imports: binascii • codecs • encodings

imported by: encodings • main.py

encodings.hp_roman8 SourceModule

imports: codecs • encodings

imported by: encodings • main.py

encodings.hz SourceModule

imports: _codecs_cn • _multibytecodec • codecs • encodings

imported by: encodings • main.py

encodings.idna SourceModule

imports: codecs • encodings • re • stringprep • unicodedata

imported by: encodings • main.py

encodings.iso2022_jp SourceModule

imports: _codecs_iso2022 • _multibytecodec • codecs • encodings

imported by: encodings • main.py

encodings.iso2022_jp_1 SourceModule

imports: _codecs_iso2022 • _multibytecodec • codecs • encodings

imported by: encodings • main.py

encodings.iso2022_jp_2 SourceModule

imports: _codecs_iso2022 • _multibytecodec • codecs • encodings

imported by: encodings • main.py

encodings.iso2022_jp_2004 SourceModule

imports: _codecs_iso2022 • _multibytecodec • codecs • encodings

imported by: encodings • main.py

encodings.iso2022_jp_3 SourceModule

imports: _codecs_iso2022 • _multibytecodec • codecs • encodings

imported by: encodings • main.py

encodings.iso2022_jp_ext SourceModule

imports: _codecs_iso2022 • _multibytecodec • codecs • encodings

imported by: encodings • main.py

encodings.iso2022_kr SourceModule

imports: _codecs_iso2022 • _multibytecodec • codecs • encodings

imported by: encodings • main.py

encodings.iso8859_1 SourceModule

imports: codecs • encodings

imported by: encodings • main.py

encodings.iso8859_10 SourceModule

imports: codecs • encodings

imported by: encodings • main.py

encodings.iso8859_11 SourceModule

imports: codecs • encodings

imported by: encodings • main.py

encodings.iso8859_13 SourceModule

imports: codecs • encodings

imported by: encodings • main.py

encodings.iso8859_14 SourceModule

imports: codecs • encodings

imported by: encodings • main.py

encodings.iso8859_15 SourceModule

imports: codecs • encodings

imported by: encodings • main.py

encodings.iso8859_16 SourceModule

imports: codecs • encodings

imported by: encodings • main.py

encodings.iso8859_2 SourceModule

imports: codecs • encodings

imported by: encodings • main.py

encodings.iso8859_3 SourceModule

imports: codecs • encodings

imported by: encodings • main.py

encodings.iso8859_4 SourceModule

imports: codecs • encodings

imported by: encodings • main.py

encodings.iso8859_5 SourceModule

imports: codecs • encodings

imported by: encodings • main.py

encodings.iso8859_6 SourceModule

imports: codecs • encodings

imported by: encodings • main.py

encodings.iso8859_7 SourceModule

imports: codecs • encodings

imported by: encodings • main.py

encodings.iso8859_8 SourceModule

imports: codecs • encodings

imported by: encodings • main.py

encodings.iso8859_9 SourceModule

imports: codecs • encodings

imported by: encodings • main.py

encodings.johab SourceModule

imports: _codecs_kr • _multibytecodec • codecs • encodings

imported by: encodings • main.py

encodings.koi8_r SourceModule

imports: codecs • encodings

imported by: encodings • main.py

encodings.koi8_t SourceModule

imports: codecs • encodings

imported by: encodings • main.py

encodings.koi8_u SourceModule

imports: codecs • encodings

imported by: encodings • main.py

encodings.kz1048 SourceModule

imports: codecs • encodings

imported by: encodings • main.py

encodings.latin_1 SourceModule

imports: codecs • encodings

imported by: encodings • main.py

encodings.mac_arabic SourceModule

imports: codecs • encodings

imported by: encodings • main.py

encodings.mac_croatian SourceModule

imports: codecs • encodings

imported by: encodings • main.py

encodings.mac_cyrillic SourceModule

imports: codecs • encodings

imported by: encodings • main.py

encodings.mac_farsi SourceModule

imports: codecs • encodings

imported by: encodings • main.py

encodings.mac_greek SourceModule

imports: codecs • encodings

imported by: encodings • main.py

encodings.mac_iceland SourceModule

imports: codecs • encodings

imported by: encodings • main.py

encodings.mac_latin2 SourceModule

imports: codecs • encodings

imported by: encodings • main.py

encodings.mac_roman SourceModule

imports: codecs • encodings

imported by: encodings • main.py

encodings.mac_romanian SourceModule

imports: codecs • encodings

imported by: encodings • main.py

encodings.mac_turkish SourceModule

imports: codecs • encodings

imported by: encodings • main.py

encodings.mbcs SourceModule

imports: codecs • encodings

imported by: encodings • main.py

encodings.oem SourceModule

imports: codecs • encodings

imported by: encodings • main.py

encodings.palmos SourceModule

imports: codecs • encodings

imported by: encodings • main.py

encodings.ptcp154 SourceModule

imports: codecs • encodings

imported by: encodings • main.py

encodings.punycode SourceModule

imports: codecs • encodings

imported by: encodings • main.py

encodings.quopri_codec SourceModule

imports: codecs • encodings • io • quopri

imported by: encodings • main.py

encodings.raw_unicode_escape SourceModule

imports: codecs • encodings

imported by: encodings • main.py

encodings.rot_13 SourceModule

imports: codecs • encodings • sys

imported by: encodings • main.py

encodings.shift_jis SourceModule

imports: _codecs_jp • _multibytecodec • codecs • encodings

imported by: encodings • main.py

encodings.shift_jis_2004 SourceModule

imports: _codecs_jp • _multibytecodec • codecs • encodings

imported by: encodings • main.py

encodings.shift_jisx0213 SourceModule

imports: _codecs_jp • _multibytecodec • codecs • encodings

imported by: encodings • main.py

encodings.tis_620 SourceModule

imports: codecs • encodings

imported by: encodings • main.py

encodings.undefined SourceModule

imports: codecs • encodings

imported by: encodings • main.py

encodings.unicode_escape SourceModule

imports: codecs • encodings

imported by: encodings • main.py

encodings.utf_16 SourceModule

imports: codecs • encodings • sys

imported by: encodings • main.py

encodings.utf_16_be SourceModule

imports: codecs • encodings

imported by: encodings • main.py

encodings.utf_16_le SourceModule

imports: codecs • encodings

imported by: encodings • main.py

encodings.utf_32 SourceModule

imports: codecs • encodings • sys

imported by: encodings • main.py

encodings.utf_32_be SourceModule

imports: codecs • encodings

imported by: encodings • main.py

encodings.utf_32_le SourceModule

imports: codecs • encodings

imported by: encodings • main.py

encodings.utf_7 SourceModule

imports: codecs • encodings

imported by: encodings • main.py

encodings.utf_8 SourceModule

imports: codecs • encodings

imported by: encodings • main.py

encodings.utf_8_sig SourceModule

imports: codecs • encodings

imported by: encodings • main.py

encodings.uu_codec SourceModule

imports: binascii • codecs • encodings • io

imported by: encodings • main.py

encodings.zlib_codec SourceModule

imports: codecs • encodings • zlib

imported by: encodings • main.py

enum SourceModule

imports: builtins • inspect • sys • types

imported by: PyQt6.QtCore • PyQt6.QtGui • PyQt6.QtOpenGL • PyQt6.QtOpenGLWidgets • PyQt6.QtSvg • PyQt6.QtTest • PyQt6.QtWidgets • _ast_unparse • annotationlib • asyncio.constants • asyncio.locks • asyncio.runners • asyncio.sslproto • asyncio.timeouts • calendar • compression.zstd • http • inspect • main.py • numpy.__config__ • numpy._globals • numpy.f2py.symbolic • pstats • py_compile • pyqtgraph.graphicsItems.PColorMeshItem • pyqtgraph.parametertree.parameterTypes.qtenum • pyqtgraph.widgets.RemoteGraphicsView • re • scipy.__config__ • scipy._lib._array_api_override • scipy._lib.array_api_compat.common._helpers • scipy._lib.array_api_extra._lib._at • scipy._lib.array_api_extra.testing • scipy._lib.cobyqa.settings • scipy._lib.pyprima • signal • socket • ssl

errno (builtin module)

imported by: asyncio.base_events • asyncio.selector_events • asyncio.unix_events • asyncio.windows_events • gettext • gzip • http.client • multiprocessing.connection • multiprocessing.forkserver • multiprocessing.queues • multiprocessing.shared_memory • numpy.f2py._backends._meson • pathlib • pathlib._os • posixpath • serial.serialposix • shutil • socket • ssl • subprocess • tempfile • xmlrpc.client

faulthandler (builtin module)

imported by: pyqtgraph.debug

fcntl MissingModule

imported by: pathlib._os • serial.serialposix • subprocess

fileinput SourceModule

imports: bz2 • getopt • gzip • io • os • sys • types • warnings

imported by: numpy.f2py.crackfortran

fnmatch SourceModule

imports: functools • itertools • os • posixpath • re

imported by: bdb • glob • shutil • tracemalloc • unittest.loader • urllib.request

fractions SourceModule

imports: decimal • functools • math • numbers • operator • re • sys

imported by: statistics

ftplib SourceModule

imports: netrc • re • socket • ssl • sys

imported by: urllib.request

functools SourceModule

imports: _functools • _thread • abc • annotationlib • collections • operator • os • reprlib • types • typing • warnings • weakref

imported by: PyQt6.uic.compile_ui • _py_warnings • _pyrepl.utils • asyncio.format_helpers • asyncio.runners • asyncio.selector_events • asyncio.tasks • asyncio.threads • asyncio.windows_events • bdb • concurrent.futures.process • contextlib • email._encoded_words • email.charset • fnmatch • fractions • glob • importlib.metadata • importlib.metadata._adapters • importlib.metadata._functools • importlib.resources._common • inspect • ipaddress • locale • main.py • multiprocessing.reduction • multiprocessing.shared_memory • numpy._core._ufunc_config • numpy._core.arrayprint • numpy._core.defchararray • numpy._core.fromnumeric • numpy._core.function_base • numpy._core.multiarray • numpy._core.numeric • numpy._core.overrides • numpy._core.shape_base • numpy._core.strings • numpy._utils • numpy.f2py.auxfuncs • numpy.fft._pocketfft • numpy.lib._arraysetops_impl • numpy.lib._arrayterator_impl • numpy.lib._function_base_impl • numpy.lib._histograms_impl • numpy.lib._index_tricks_impl • numpy.lib._nanfunctions_impl • numpy.lib._npyio_impl • numpy.lib._polynomial_impl • numpy.lib._shape_base_impl • numpy.lib._twodim_base_impl • numpy.lib._type_check_impl • numpy.lib._utils_impl • numpy.linalg._linalg • numpy.ma.core • numpy.polynomial.polyutils • numpy.testing._private.utils • operator • pickle • pkgutil • platform • pstats • pyqtgraph.graphicsItems.GraphicsItem • pyqtgraph.parametertree.interactive • re • scipy._lib._array_api • scipy._lib._array_api_override • scipy._lib._docscrape • scipy._lib._uarray._backend • scipy._lib._util • scipy._lib.array_api_compat._internal • scipy._lib.array_api_compat.common._helpers • scipy._lib.array_api_compat.torch._aliases • scipy._lib.array_api_compat.torch._info • scipy._lib.array_api_extra._lib._lazy • scipy._lib.array_api_extra._lib._utils._helpers • scipy._lib.array_api_extra.testing • scipy._lib.deprecation • scipy.fft._helper • scipy.fft._pocketfft.basic • scipy.fft._pocketfft.realtransforms • scipy.integrate._quad_vec • scipy.integrate._quadpack_py • scipy.integrate._rules._base • scipy.integrate._rules._gauss_kronrod • scipy.integrate._rules._gauss_legendre • scipy.integrate._rules._genz_malik • scipy.interpolate._ndbspline • scipy.linalg.blas • scipy.ndimage._support_alternative_backends • scipy.optimize._differentialevolution • scipy.optimize._numdiff • scipy.optimize._shgo_lib._complex • scipy.signal._short_time_fft • scipy.signal._support_alternative_backends • scipy.spatial.distance • scipy.special._spherical_bessel • scipy.special._support_alternative_backends • scipy.stats._axis_nan_policy • scipy.stats._bws_test • scipy.stats._continuous_distns • scipy.stats._covariance • scipy.stats._discrete_distns • scipy.stats._distribution_infrastructure • scipy.stats._levy_stable • scipy.stats._qmc • scipy.stats.contingency • shiboken6 • statistics • tempfile • tokenize • tracemalloc • types • typing • unittest.case • unittest.loader • unittest.result • unittest.signals • urllib.parse

gc (builtin module)

imports: time

imported by: _posixsubprocess • numpy.testing._private.utils • pyqtgraph.debug • pyqtgraph.reload • timeit • weakref

genericpath SourceModule

imports: os • stat

imported by: main.py • ntpath • posixpath

getopt SourceModule

imports: gettext • os • sys

imported by: base64 • fileinput • pydoc • quopri • timeit

gettext SourceModule

imports: builtins • copy • errno • locale • operator • os • re • struct • sys • warnings

imported by: argparse • getopt • optparse

glob SourceModule

imports: contextlib • fnmatch • functools • itertools • operator • os • re • stat • sys • warnings

imported by: pathlib • pdb • serial.tools.list_ports_common • serial.tools.list_ports_linux • serial.tools.list_ports_posix

grp MissingModule

imported by: pathlib • shutil • subprocess • tarfile

gzip SourceModule

imports: argparse • builtins • compression._common • compression._common._streams • errno • io • os • struct • sys • time • warnings • weakref • zlib

imported by: fileinput • numpy.lib._datasource • tarfile • xmlrpc.client

h5py MissingModule

imported by: pyqtgraph.exporters.HDF5Exporter

hashlib SourceModule

imports: _blake2 • _hashlib • _md5 • _sha1 • _sha2 • _sha3 • logging

imported by: hmac • random • urllib.request

heapq SourceModule

imports: _heapq

imported by: asyncio.base_events • asyncio.queues • collections • difflib • main.py • queue • scipy.integrate._cubature • scipy.integrate._quad_vec • scipy.special._basic

hmac SourceModule

imports: _hashlib • _hmac • _operator • hashlib • warnings

imported by: multiprocessing.connection • secrets

html Package

imports: html.entities • re

imported by: html.entities • http.server

html.entities SourceModule

imports: html

imported by: html

http Package

imports: enum

imported by: http.client • http.cookiejar • http.server

http.client SourceModule

imports: 'collections.abc' • email.message • email.parser • errno • http • io • re • socket • ssl • sys • urllib.parse

imported by: http.cookiejar • http.server • urllib.request • xmlrpc.client

http.cookiejar SourceModule

imports: calendar • copy • datetime • http • http.client • io • logging • os • re • threading • time • traceback • urllib.parse • urllib.request • warnings

imported by: urllib.request

http.server SourceModule

imports: argparse • base64 • binascii • contextlib • copy • datetime • email.utils • html • http • http.client • io • itertools • mimetypes • os • posixpath • pwd • select • shutil • socket • socketserver • ssl • subprocess • sys • time • urllib.parse • warnings

imported by: pydoc

importlib Package

imports: _frozen_importlib • _frozen_importlib_external • _imp • importlib • importlib._bootstrap • importlib._bootstrap_external • importlib.machinery • sys

imported by: _pyi_rth_utils.qt • importlib • importlib._abc • importlib._bootstrap • importlib._bootstrap_external • importlib.abc • importlib.machinery • importlib.metadata • importlib.readers • importlib.resources • importlib.resources._common • importlib.util • inspect • pkgutil • pyqtgraph • pyqtgraph.Qt • pyqtgraph.Qt.OpenGLHelpers • pyqtgraph.flowchart.Flowchart • pyqtgraph.graphicsItems.PColorMeshItem • pyqtgraph.graphicsItems.PlotCurveItem • pyqtgraph.multiprocess.bootstrap • pyqtgraph.reload • pyqtgraph.widgets.RawImageWidget • scipy • scipy._lib._uarray._backend • scipy._lib.array_api_compat._internal • scipy._lib.deprecation • scipy.ndimage._support_alternative_backends • scipy.signal._support_alternative_backends • scipy.sparse • serial • sysconfig

importlib._abc SourceModule

imports: abc • importlib • importlib._bootstrap

imported by: importlib.abc • importlib.util

importlib._bootstrap SourceModule

imports: _frozen_importlib_external • importlib

imported by: importlib • importlib._abc • importlib.machinery • importlib.util • pydoc

importlib._bootstrap_external SourceModule

imports: _imp • _io • _warnings • importlib • importlib.metadata • importlib.readers • marshal • nt • posix • sys • tokenize • winreg

imported by: importlib • importlib.abc • importlib.machinery • importlib.util • py_compile • pydoc

importlib.abc SourceModule

imports: _frozen_importlib • _frozen_importlib_external • abc • importlib • importlib._abc • importlib._bootstrap_external • importlib.machinery • warnings

imported by: importlib.metadata

importlib.machinery SourceModule

imports: importlib • importlib._bootstrap • importlib._bootstrap_external • warnings

imported by: cProfile • ctypes.util • importlib • importlib.abc • inspect • pkgutil • profile • py_compile • pydoc • runpy • sysconfig

importlib.metadata Package

imports: __future__ • abc • collections • contextlib • csv • email • functools • importlib • importlib.abc • importlib.metadata • importlib.metadata._adapters • importlib.metadata._collections • importlib.metadata._functools • importlib.metadata._itertools • importlib.metadata._meta • inspect • itertools • json • operator • os • pathlib • posixpath • re • sys • textwrap • types • typing • warnings • zipfile

imported by: importlib._bootstrap_external • importlib.metadata • importlib.metadata._adapters • importlib.metadata._collections • importlib.metadata._functools • importlib.metadata._itertools • importlib.metadata._meta • importlib.metadata._text • numpy.testing._private.utils • scipy._lib.cobyqa.utils.versions

importlib.metadata._adapters SourceModule

imports: email.message • functools • importlib.metadata • importlib.metadata._text • re • textwrap • warnings

imported by: importlib.metadata

importlib.metadata._collections SourceModule

imports: collections • importlib.metadata

imported by: importlib.metadata

importlib.metadata._functools SourceModule

imports: functools • importlib.metadata • types

imported by: importlib.metadata • importlib.metadata._text

importlib.metadata._itertools SourceModule

imports: importlib.metadata • itertools

imported by: importlib.metadata

importlib.metadata._meta SourceModule

imports: __future__ • importlib.metadata • os • typing

imported by: importlib.metadata

importlib.metadata._text SourceModule

imports: importlib.metadata • importlib.metadata._functools • re

imported by: importlib.metadata._adapters

importlib.readers SourceModule

imports: importlib • importlib.resources.readers

imported by: importlib._bootstrap_external • zipimport

importlib.resources Package

imports: importlib • importlib.resources • importlib.resources._common • importlib.resources._functional • importlib.resources.abc

imported by: importlib.resources • importlib.resources._adapters • importlib.resources._common • importlib.resources._functional • importlib.resources._itertools • importlib.resources.abc • importlib.resources.readers • pyqtgraph.Qt

importlib.resources._adapters SourceModule

imports: contextlib • importlib.resources • importlib.resources.abc • io

imported by: importlib.resources._common

importlib.resources._common SourceModule

imports: contextlib • functools • importlib • importlib.resources • importlib.resources._adapters • importlib.resources.abc • inspect • itertools • os • pathlib • tempfile • types • typing • warnings

imported by: importlib.resources • importlib.resources._functional

importlib.resources._functional SourceModule

imports: importlib.resources • importlib.resources._common • warnings

imported by: importlib.resources

importlib.resources._itertools SourceModule

imports: importlib.resources

imported by: importlib.resources.readers

importlib.resources.abc SourceModule

imports: abc • importlib.resources • io • itertools • os • pathlib • typing

imported by: importlib.resources • importlib.resources._adapters • importlib.resources._common • importlib.resources.readers

importlib.resources.readers SourceModule

imports: 'collections.abc' • __future__ • collections • contextlib • importlib.resources • importlib.resources._itertools • importlib.resources.abc • itertools • operator • pathlib • re • warnings • zipfile

imported by: importlib.readers

importlib.util SourceModule

imports: _imp • importlib • importlib._abc • importlib._bootstrap • importlib._bootstrap_external • sys • threading • types

imported by: cProfile • numpy.testing._private.extbuild • pkgutil • py_compile • pydoc • pyi_rth_pyqtgraph_multiprocess.py • pyqtgraph.exporters.HDF5Exporter • pyqtgraph.widgets.ColorMapMenu • runpy • scipy._lib._testutils • sysconfig • zipfile

inspect SourceModule

imports: 'collections.abc' • abc • annotationlib • argparse • ast • builtins • collections • dis • enum • functools • importlib • importlib.machinery • itertools • keyword • linecache • operator • os • re • sys • token • tokenize • types • weakref

imported by: _py_warnings • ast • asyncio.coroutines • asyncio.format_helpers • asyncio.runners • asyncio.tasks • bdb • cmd • dataclasses • doctest • enum • importlib.metadata • importlib.resources._common • numpy.lib._utils_impl • numpy.ma.core • numpy.testing._private.utils • pdb • pkgutil • pydoc • pyi_rth_inspect.py • pyqtgraph.WidgetGroup • pyqtgraph.debug • pyqtgraph.multiprocess.processes • pyqtgraph.parametertree.interactive • pyqtgraph.reload • rlcompleter • scipy._lib._docscrape • scipy._lib._testutils • scipy._lib._uarray._backend • scipy._lib._util • scipy._lib.array_api_compat._internal • scipy._lib.array_api_compat.common._aliases • scipy._lib.array_api_compat.common._helpers • scipy._lib.cobyqa.problem • scipy._lib.cobyqa.subsolvers.geometry • scipy._lib.cobyqa.subsolvers.optim • scipy._lib.deprecation • scipy.fft._helper • scipy.integrate._ivp.ivp • scipy.optimize._basinhopping • scipy.optimize._linprog_highs • scipy.optimize._nonlin • scipy.stats._axis_nan_policy • scipy.stats._distribution_infrastructure • scipy.stats._resampling • scipy.stats._sensitivity_analysis • typing • unittest.async_case • unittest.case

io SourceModule

imports: _collections_abc • _io • abc

imported by: PyQt6.uic.load_ui • _colorize • _pyrepl.pager • _pyrepl.utils • asyncio.graph • asyncio.proactor_events • asyncio.unix_events • bz2 • cProfile • compression._common._streams • compression.zstd._zstdfile • csv • dis • doctest • email.feedparser • email.generator • email.iterators • email.message • email.parser • encodings.quopri_codec • encodings.uu_codec • fileinput • gzip • http.client • http.cookiejar • http.server • importlib.resources._adapters • importlib.resources.abc • logging • lzma • main.py • multiprocessing.connection • multiprocessing.popen_forkserver • multiprocessing.popen_spawn_posix • multiprocessing.reduction • numpy.lib._format_impl • numpy.testing._private.utils • os • pathlib • pathlib._os • pdb • pickle • pprint • profile • pydoc • quopri • runpy • scipy._lib.array_api_extra._lib._utils._helpers • serial.serialutil • shiboken6 • shlex • socket • socketserver • subprocess • tarfile • tempfile • tokenize • traceback • unittest.result • urllib.error • urllib.request • xml.dom.minidom • xml.dom.pulldom • xml.etree.ElementTree • xml.sax • xml.sax.saxutils • xmlrpc.client • zipfile • zipfile._path

ipaddress SourceModule

imports: functools • re

imported by: urllib.parse • urllib.request

itertools (builtin module)

imported by: _pydecimal • asyncio.base_events • asyncio.selector_events • asyncio.tasks • asyncio.unix_events • asyncio.windows_utils • calendar • collections • concurrent.futures._base • concurrent.futures.process • concurrent.futures.thread • ctypes.macholib.dyld • dataclasses • fnmatch • glob • http.server • importlib.metadata • importlib.metadata._itertools • importlib.resources._common • importlib.resources.abc • importlib.resources.readers • inspect • multiprocessing.connection • multiprocessing.pool • multiprocessing.process • multiprocessing.util • numpy._core.einsumfunc • numpy._core.numeric • numpy._core.shape_base • numpy.f2py._backends._meson • numpy.lib._iotools • numpy.lib._npyio_impl • numpy.lib.recfunctions • numpy.ma.extras • pathlib • pdb • pickle • platform • pyqtgraph.Qt.internals • pyqtgraph.exporters.CSVExporter • pyqtgraph.graphicsItems.ScatterPlotItem • random • reprlib • scipy._lib._pep440 • scipy.integrate._cubature • scipy.integrate._ivp.common • scipy.integrate._rules._genz_malik • scipy.interpolate._bsplines • scipy.interpolate._ndbspline • scipy.interpolate._rbfinterp_common • scipy.interpolate._rgi • scipy.linalg._basic • scipy.linalg._decomp_lu • scipy.linalg._matfuncs • scipy.ndimage._interpolation • scipy.optimize._qap • scipy.optimize._shgo_lib._complex • scipy.sparse._compressed • scipy.sparse._dok • scipy.stats._distn_infrastructure • scipy.stats._hypotests • scipy.stats._morestats • scipy.stats._mstats_basic • scipy.stats._page_trend_test • scipy.stats._resampling • scipy.stats._stats_py • statistics • threading • timeit • tokenize • traceback • weakref • zipfile._path

java MissingModule

imported by: platform

jax MissingModule

imported by: scipy._lib._array_api • scipy._lib.array_api_compat.common._helpers • scipy._lib.array_api_extra._lib._lazy • scipy._lib.array_api_extra._lib._utils._helpers

json Package

imports: codecs • json.decoder • json.encoder • json.scanner

imported by: controller • importlib.metadata • json.decoder • json.encoder • json.scanner • numpy.__config__ • numpy.testing._private.utils • pdb • scipy.__config__

json.decoder SourceModule

imports: _json • json • json.scanner • re

imported by: _json • json

json.encoder SourceModule

imports: _json • json • re

imported by: json

json.scanner SourceModule

imports: _json • json • re

imported by: json • json.decoder

keyword SourceModule

imported by: _pyrepl.utils • annotationlib • collections • dataclasses • inspect • main.py • rlcompleter • scipy._lib._bunch • scipy.stats._distn_infrastructure • shiboken6 • traceback

linecache SourceModule

imports: os • sys • tokenize

imported by: _py_warnings • asyncio.base_tasks • bdb • doctest • inspect • main.py • pdb • timeit • traceback • tracemalloc

locale SourceModule

imports: _collections_abc • _locale • builtins • encodings • encodings.aliases • functools • os • re • sys • warnings

imported by: _pydecimal • _strptime • calendar • gettext • main.py • subprocess

logging Package

imports: 'collections.abc' • atexit • io • os • pickle • re • string • sys • threading • time • traceback • types • warnings • weakref

imported by: PyQt6.uic.Compiler.qobjectcreator • PyQt6.uic.properties • PyQt6.uic.uiparser • asyncio.futures • asyncio.log • concurrent.futures._base • controller • hashlib • http.cookiejar • main.py • modules.serial_manager • multiprocessing.util • scipy.optimize._shgo • scipy.optimize._shgo_lib._complex • unittest._log

lzma SourceModule

imports: _lzma • builtins • compression._common • compression._common._streams • io • os

imported by: numpy.lib._datasource • shutil • tarfile • zipfile

marshal (builtin module)

imported by: cProfile • importlib._bootstrap_external • pkgutil • profile • pstats • shiboken6 • zipimport

math (builtin module)

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

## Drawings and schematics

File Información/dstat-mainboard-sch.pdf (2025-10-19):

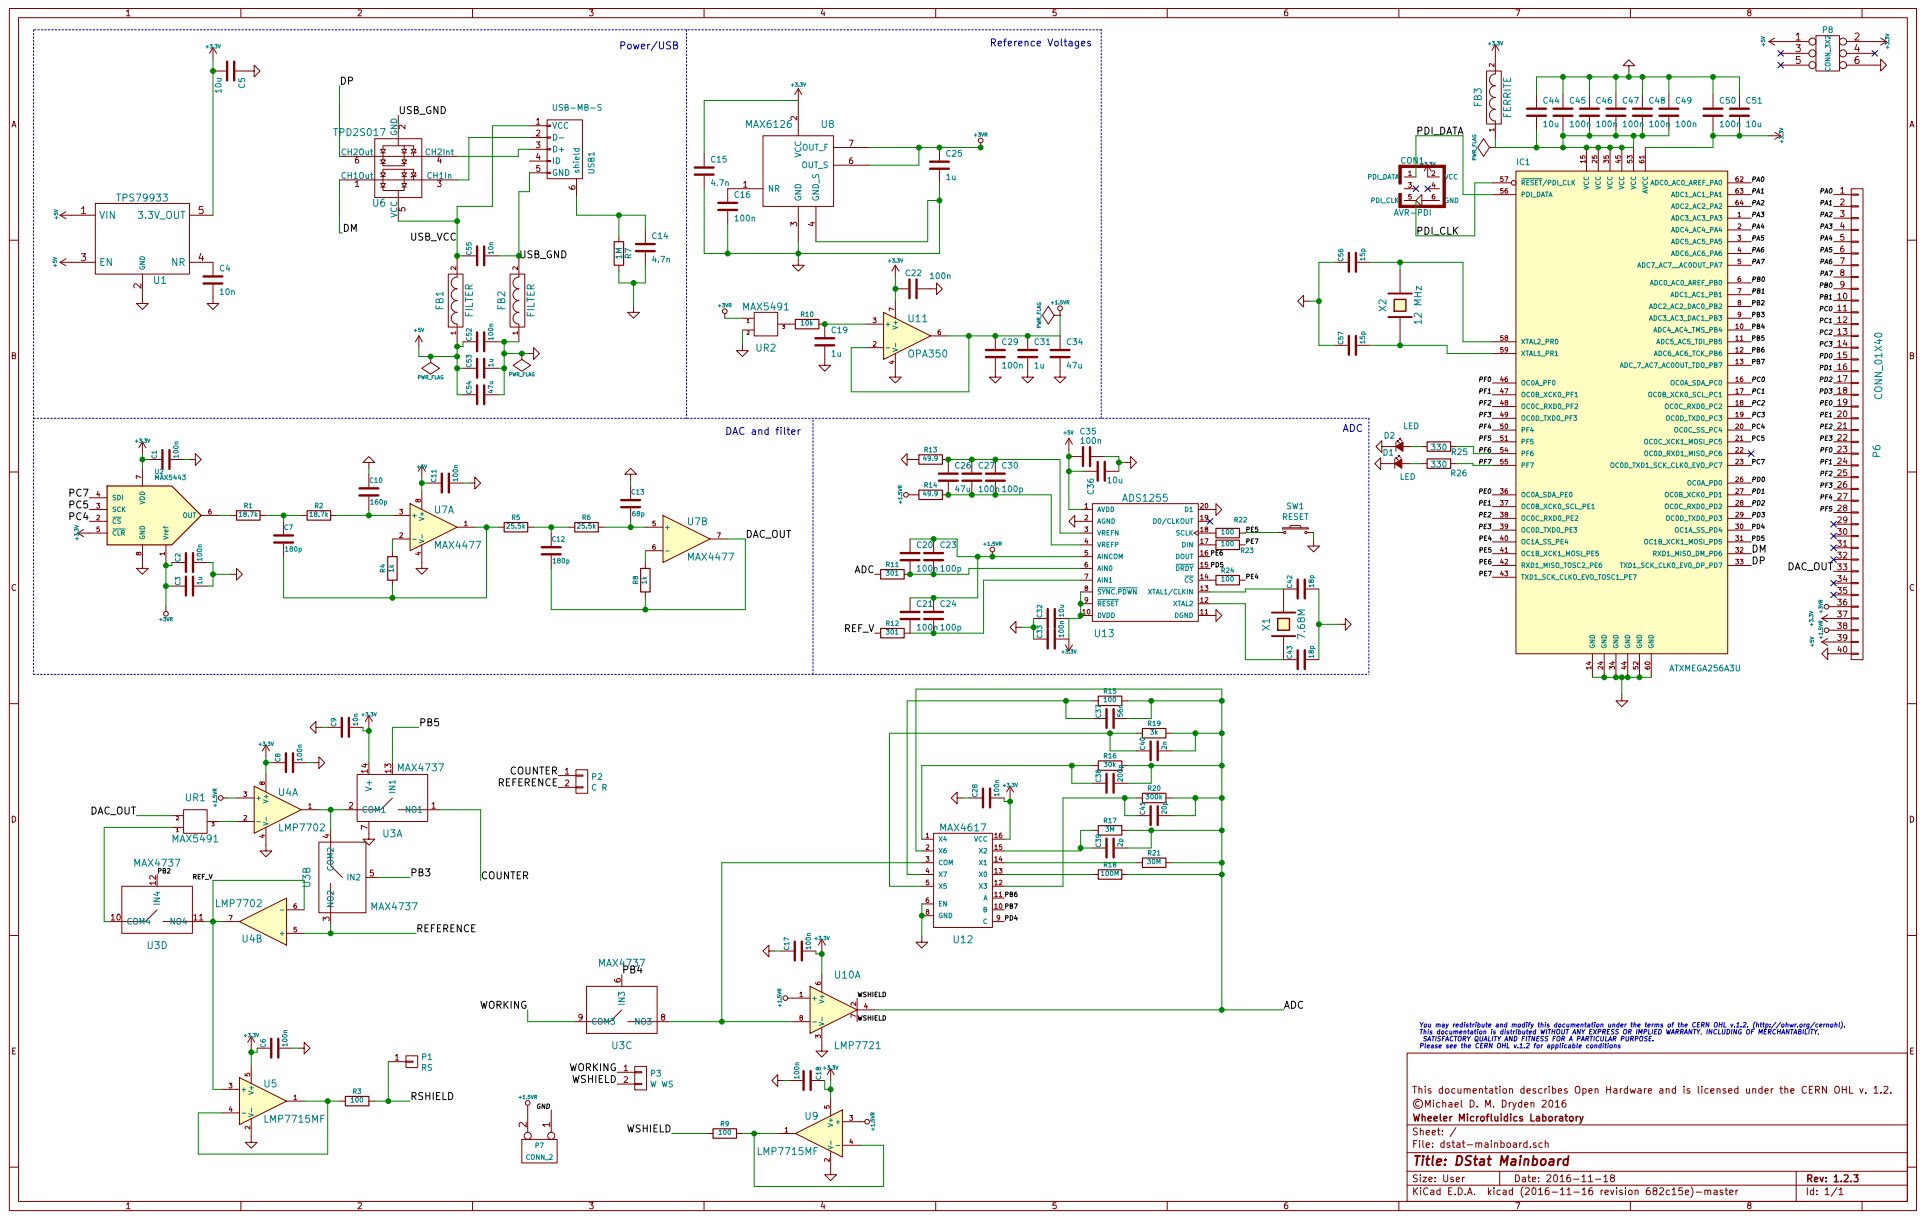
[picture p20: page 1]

You may redistribute and modify this documentation under the terms of the CERN OHL v.1.2. (http://ohwr.org/cernohl).
This documentation is distributed WITHOUT ANY EXPRESS OR IMPLIED WARRANTY, INCLUDING OF MERCHANTABILITY,
SATISFACTORY QUALITY AND FITNESS FOR A PARTICULAR PURPOSE.
Please see the CERN OHL v.1.2 for applicable conditions

This documentation describes Open Hardware and is licensed under the CERN OHL v. 1.2.
©Michael D. M. Dryden 2016
Wheeler Microfluidics Laboratory
Sheet: /
File: dstat-mainboard.sch
Title: DStat Mainboard

KiCad E.D.A. kicad (2016-11-16 revision 682c15e)-master

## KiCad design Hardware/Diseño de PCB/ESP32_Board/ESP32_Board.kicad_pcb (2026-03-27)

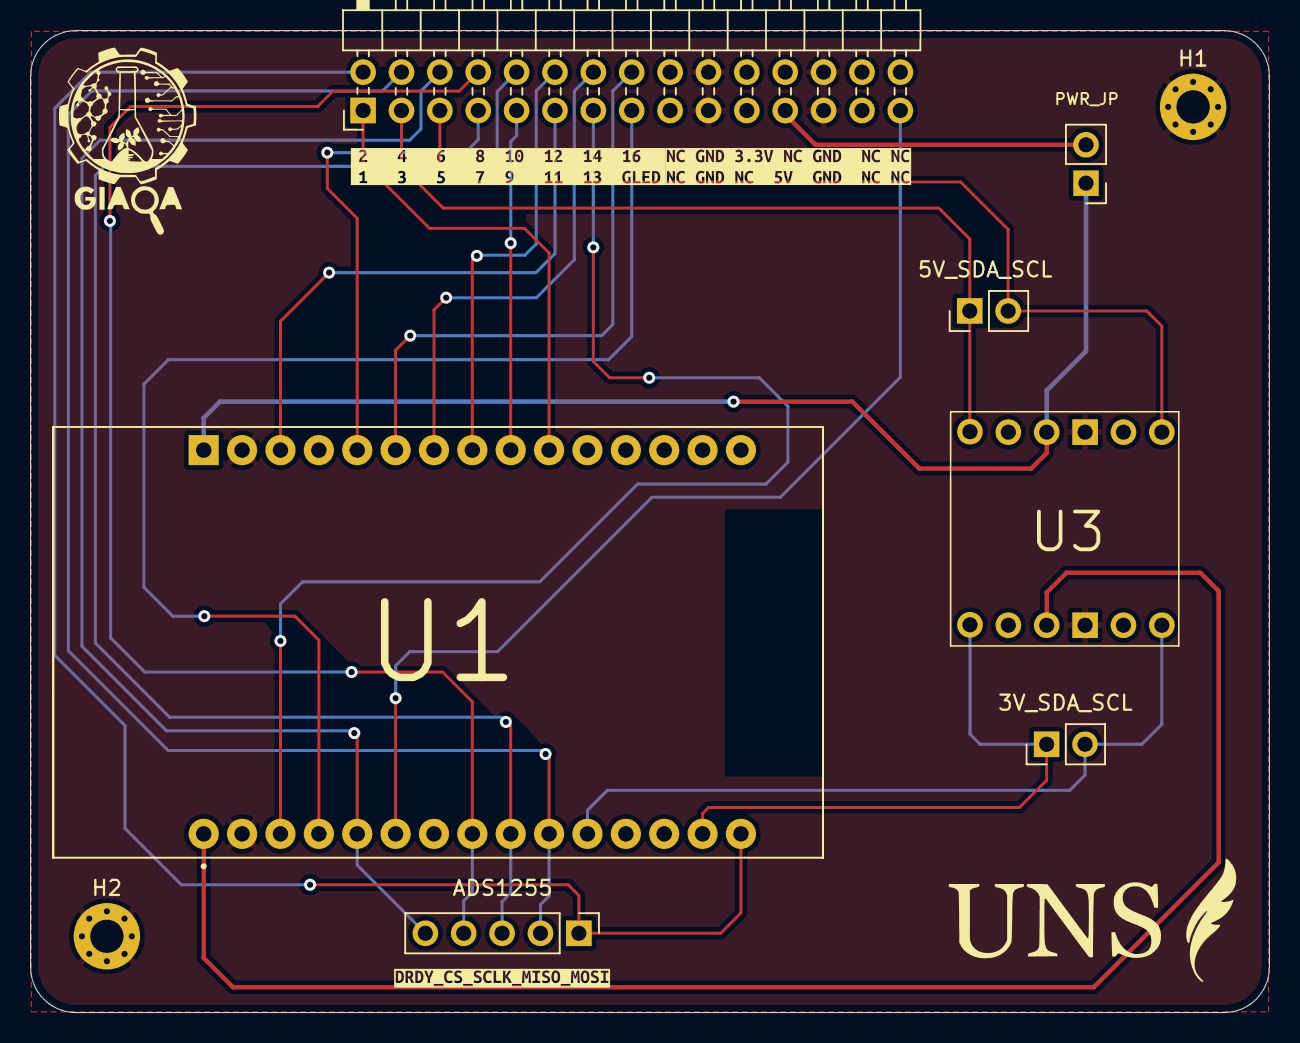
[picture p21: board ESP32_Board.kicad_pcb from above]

Board: 2 copper layers, 82.0 x 65.0 mm, 13 parts (0 on the bottom side), 23 nets.

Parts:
3V_SDA_SCL, 5V_SDA_SCL: Conn_01x02; PinHeader_1x02_P2.54mm_Vertical
ADS1255: Conn_01x05; PinHeader_1x05_P2.54mm_Vertical
H1, H2: MountingHole_Pad; MountingHole_2.2mm_M2_Pad_Via
J1: Conn_02x15_Odd_Even; PinHeader_2x15_P2.54mm_Horizontal
PWR_JP: Jumper_2_Open; PinHeader_1x02_P2.54mm_Vertical
U1: ESP32 - DEVKIT; MODULE_ESP32_DEVKIT_V1_CORRECTED
U2: logo; logo_uns
U3: LevelShifter
kibuzzard-69A1DE73: G***; kibuzzard-69A1DE73
kibuzzard-69A5AE09: G***; kibuzzard-69A5AE09
kibuzzard-69C42740: G***; kibuzzard-69C42740

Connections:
+3.3V: U1.2 (3V3), U3.3 (3.3V)
+5V: PWR_JP.1 (A), U1.0 (VIN), U3.10 (5V)
/5V: J1.23, PWR_JP.2 (B)
/ADS1255_CLOCK_PIN: J1.29, U1.27 (RX2/D16)
/ADS1255_CS: ADS1255.4, J1.8, U1.29 (D5)
/ADS1255_DIN_MOSI: ADS1255.1, J1.2, U1.37 (D23)
/ADS1255_DOUT_MISO: ADS1255.2, J1.4, U1.31 (D19)
/ADS1255_DRDY: ADS1255.5, J1.6, U1.26 (D4)
/ADS1255_SCLK: ADS1255.3, J1.10, U1.30 (D18)
/GREEN_LED: J1.15, U1.24 (D2)
/MAX4617_SEL_A: J1.16, U1.12 (D27)
/MAX4617_SEL_B: J1.14, U1.11 (D26)
/MAX4617_SEL_C: J1.12, U1.10 (D25)
/MAX4737_CE_EN: J1.13, U1.23 (D15)
/MAX4737_CR_SHORT_EN: J1.7, U1.13 (D14)
/MAX4737_RE_FB_EN: J1.9, U1.9 (D33)
/MAX4737_WE_EN: J1.11, U1.16 (D13)
/MAX_5217_NAUX: J1.1, U1.8 (D32)
/MAX_5217_SCL: 3V_SDA_SCL.1, U1.36 (D22), U3.1 (TXI1)
/MAX_5217_SDA: 3V_SDA_SCL.2, U1.33 (D21), U3.6 (TXI2)
/TO_DAC_SCL_PIN_3: 5V_SDA_SCL.1, J1.3, U3.12 (TXD1)
/TO_DAC_SDA_PIN_5: 5V_SDA_SCL.2, J1.5, U3.7 (TXD2)
GND: H1.1, H2.1, J1.19, J1.20, J1.25, J1.26, U1.1 (GND), U1.38 (GND), U3.4 (GND), U3.9 (GND)

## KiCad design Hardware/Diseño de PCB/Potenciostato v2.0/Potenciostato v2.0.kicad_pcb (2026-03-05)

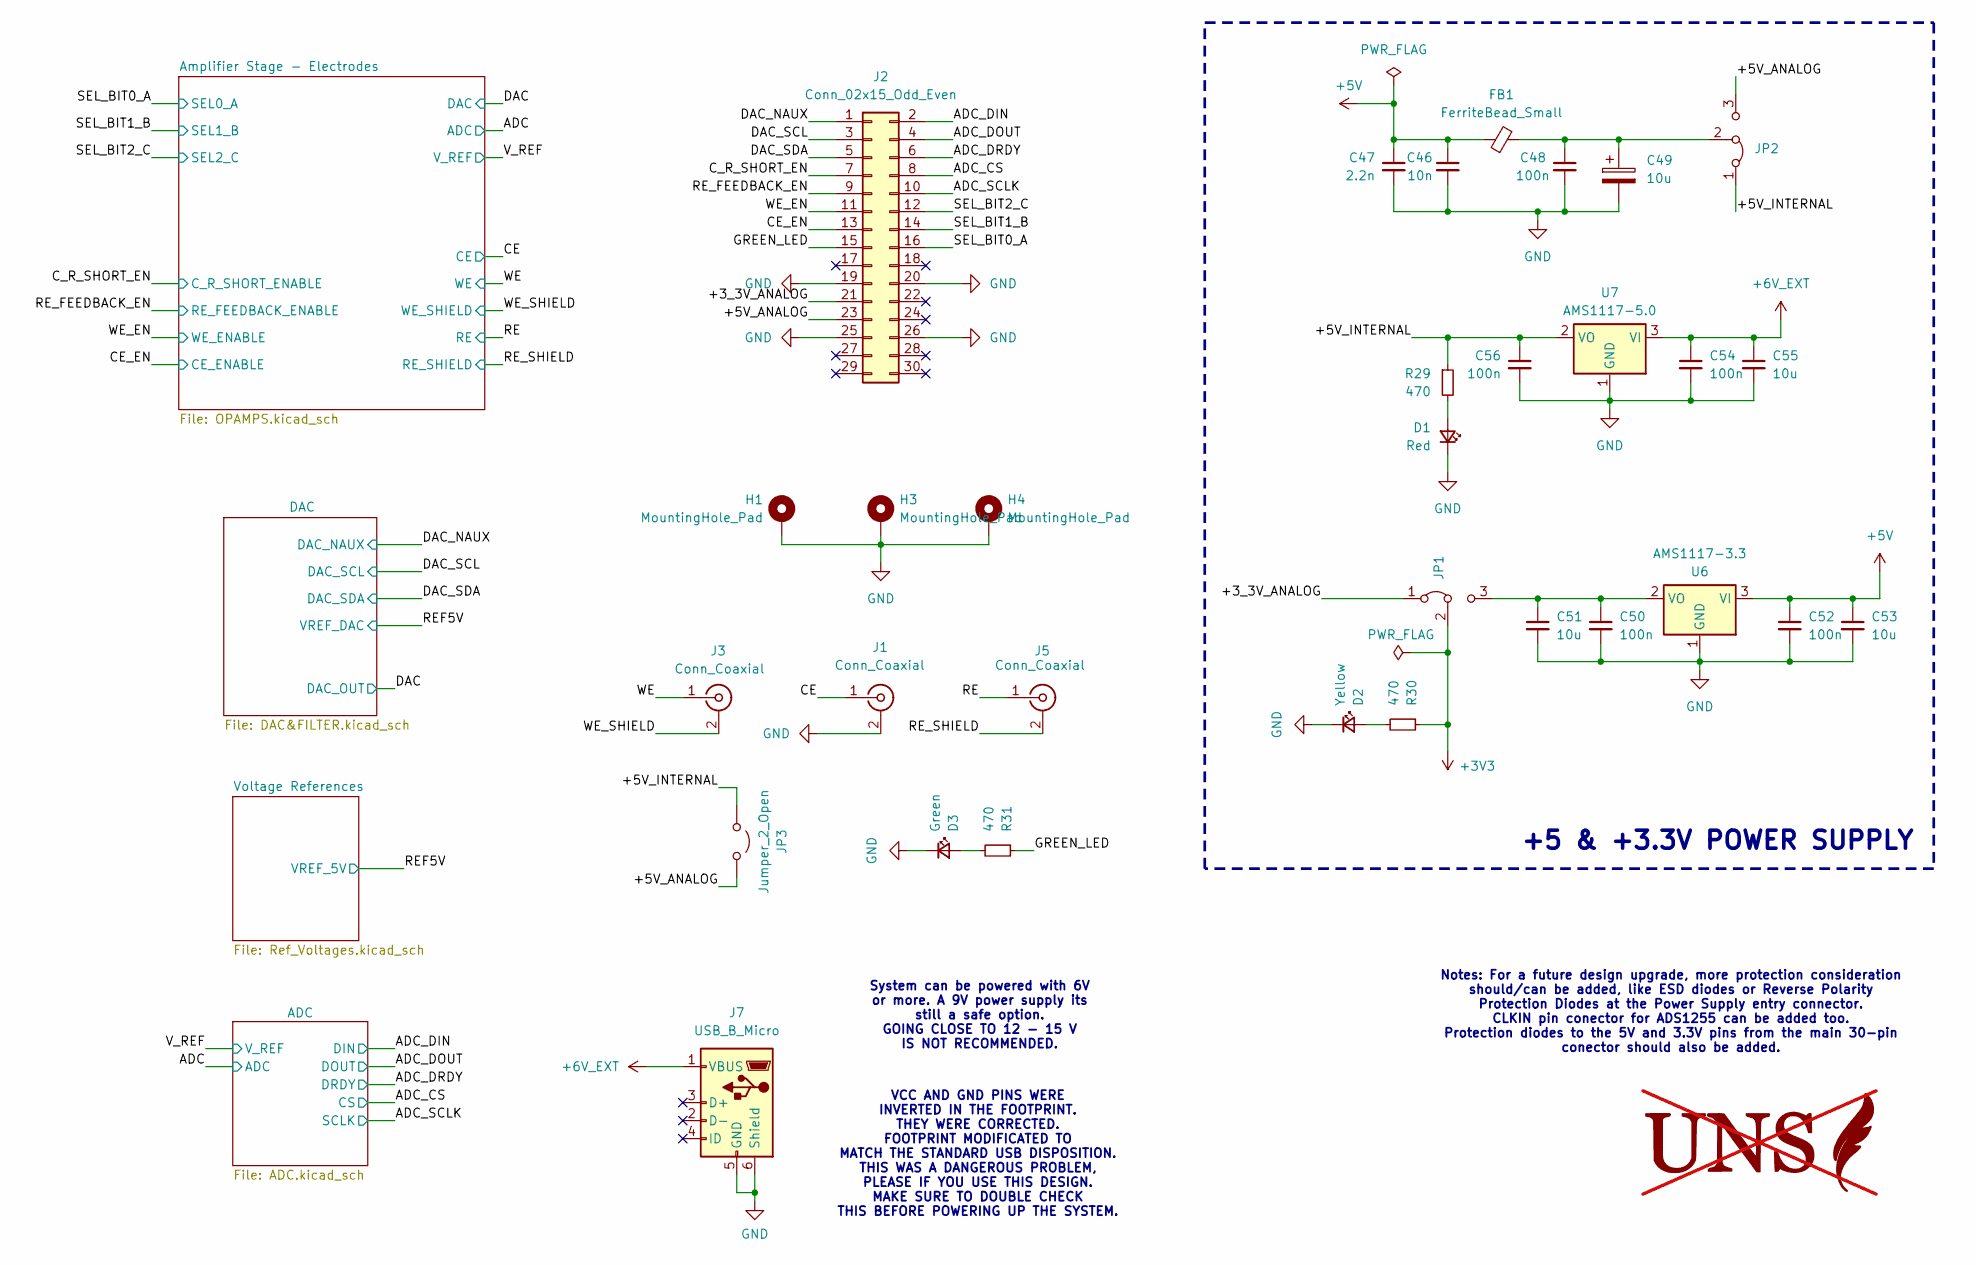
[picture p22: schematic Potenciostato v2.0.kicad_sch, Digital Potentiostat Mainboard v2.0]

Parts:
C46: 10n; C_0805_2012Metric_Pad1.18x1.45mm_HandSolder
C47: 2.2n; C_1206_3216Metric_Pad1.33x1.80mm_HandSolder
C48, C50, C52, C54, C56: 100n; C_0805_2012Metric_Pad1.18x1.45mm_HandSolder
C49: 10u; CP_Elec_4x5.4
C51, C53, C55: 10u; CP_EIA-6032-20_AVX-F_Pad2.25x2.35mm_HandSolder
D1: Red; LED_1206_3216Metric_Pad1.42x1.75mm_HandSolder
D2: Yellow; LED_1206_3216Metric_Pad1.42x1.75mm_HandSolder
D3: Green; LED_1206_3216Metric_Pad1.42x1.75mm_HandSolder
FB1: FerriteBead_Small; L_0603_1608Metric_Pad1.05x0.95mm_HandSolder; MFR.Part # PZ1608D102-R80TF; JLCPCB Part # C279752
H1, H3, H4: MountingHole_Pad; MountingHole_2.2mm_M2_Pad_Via
J1, J3, J5: Conn_Coaxial; BNC_Amphenol_B6252HB-NPP3G-50_Horizontal
J2: Conn_02x15_Odd_Even; PinSocket_2x15_P2.54mm_Horizontal
J7: USB_B_Micro; USB_Micro-B_GCT_USB3076-30-A
JP1, JP2: Jumper_3_Bridged12; PinHeader_1x03_P2.54mm_Vertical
JP3: Jumper_2_Open; TestPoint_2Pads_Pitch2.54mm_Drill0.8mm
R29, R30, R31: 470; R_0603_1608Metric_Pad0.98x0.95mm_HandSolder
U6: AMS1117-3.3; SOT-223-3_TabPin2
U7: AMS1117-5.0; SOT-223-3_TabPin2
U8: not fitted

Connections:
+3V3: JP1.2 (C), R30.1; also elsewhere on the board
+5V: C46.1, C47.1, C52.1, C53.1, FB1.1, U6.3 (VI); also elsewhere on the board
+6V_EXT: C54.1, C55.1, J7.1 (VBUS), U7.3 (VI); also elsewhere on the board
/+3_3V_ANALOG: J2.21, JP1.1 (A)
/+5V_ANALOG: J2.23, JP2.3 (B), JP3.2 (B)
/+5V_INTERNAL: C56.1, JP2.1 (A), JP3.1 (A), R29.1, U7.2 (VO)
/ADC_CS: J2.8; also elsewhere on the board
/ADC_DIN: J2.2; also elsewhere on the board
/ADC_DOUT: J2.4; also elsewhere on the board
/ADC_DRDY: J2.6; also elsewhere on the board
/ADC_SCLK: J2.10; also elsewhere on the board
/CE: J1.1 (In); also elsewhere on the board
/CE_EN: J2.13; also elsewhere on the board
/C_R_SHORT_EN: J2.7; also elsewhere on the board
/DAC_NAUX: J2.1; also elsewhere on the board
/DAC_SCL: J2.3; also elsewhere on the board
/DAC_SDA: J2.5; also elsewhere on the board
/GREEN_LED: J2.15, R31.1
/RE: J5.1 (In); also elsewhere on the board
/RE_FEEDBACK_EN: J2.9; also elsewhere on the board
/RE_SHIELD: J5.2 (Ext); also elsewhere on the board
/SEL_BIT0: J2.16; also elsewhere on the board
/SEL_BIT1: J2.14; also elsewhere on the board
/SEL_BIT2: J2.12; also elsewhere on the board
/WE: J3.1 (In); also elsewhere on the board
/WE_EN: J2.11; also elsewhere on the board
/WE_SHIELD: J3.2 (Ext); also elsewhere on the board
GND: C46.2, C47.2, C48.2, C49.2, C50.2, C51.2, C52.2, C53.2, C54.2, C55.2, C56.2, D1.1 (K), D2.1 (K), D3.1 (K), H1.1, H3.1, H4.1, J1.2 (Ext), J2.19, J2.20, J2.25, J2.26, J7.5 (GND), J7.6 (Shield), U6.1 (GND), U7.1 (GND); also elsewhere on the board
unnamed: D1.2 (A), R29.2
unnamed: D2.2 (A), R30.2
unnamed: D3.2 (A), R31.2
unnamed: C50.1, C51.1, JP1.3 (B), U6.2 (VO)
unnamed: C48.1, C49.1, FB1.2, JP2.2 (C)

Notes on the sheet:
+5 & +3.3V POWER SUPPLY
Notes: For a future design upgrade, more protection consideration should/can be added, like ESD diodes or Reverse Polarity Protection Diodes at the Power Supply entry connector. CLKIN pin conector for ADS1255 can be added too. Protection diodes to the 5V and 3.3V pins from the main 30-pin conector 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
VCC AND GND PINS WERE INVERTED IN THE FOOTPRINT. THEY WERE CORRECTED. FOOTPRINT MODIFICATED TO MATCH THE STANDARD USB DISPOSITION. THIS WAS A DANGEROUS PROBLEM, PLEASE IF YOU USE THIS DESIGN. MAKE SURE TO DOUBLE CHECK THIS BEFORE POWERING UP THE SYSTEM.
System can be powered with 6V or more. A 9V power supply its still a safe option. GOING CLOSE TO 12 - 15 V IS NOT RECOMMENDED.

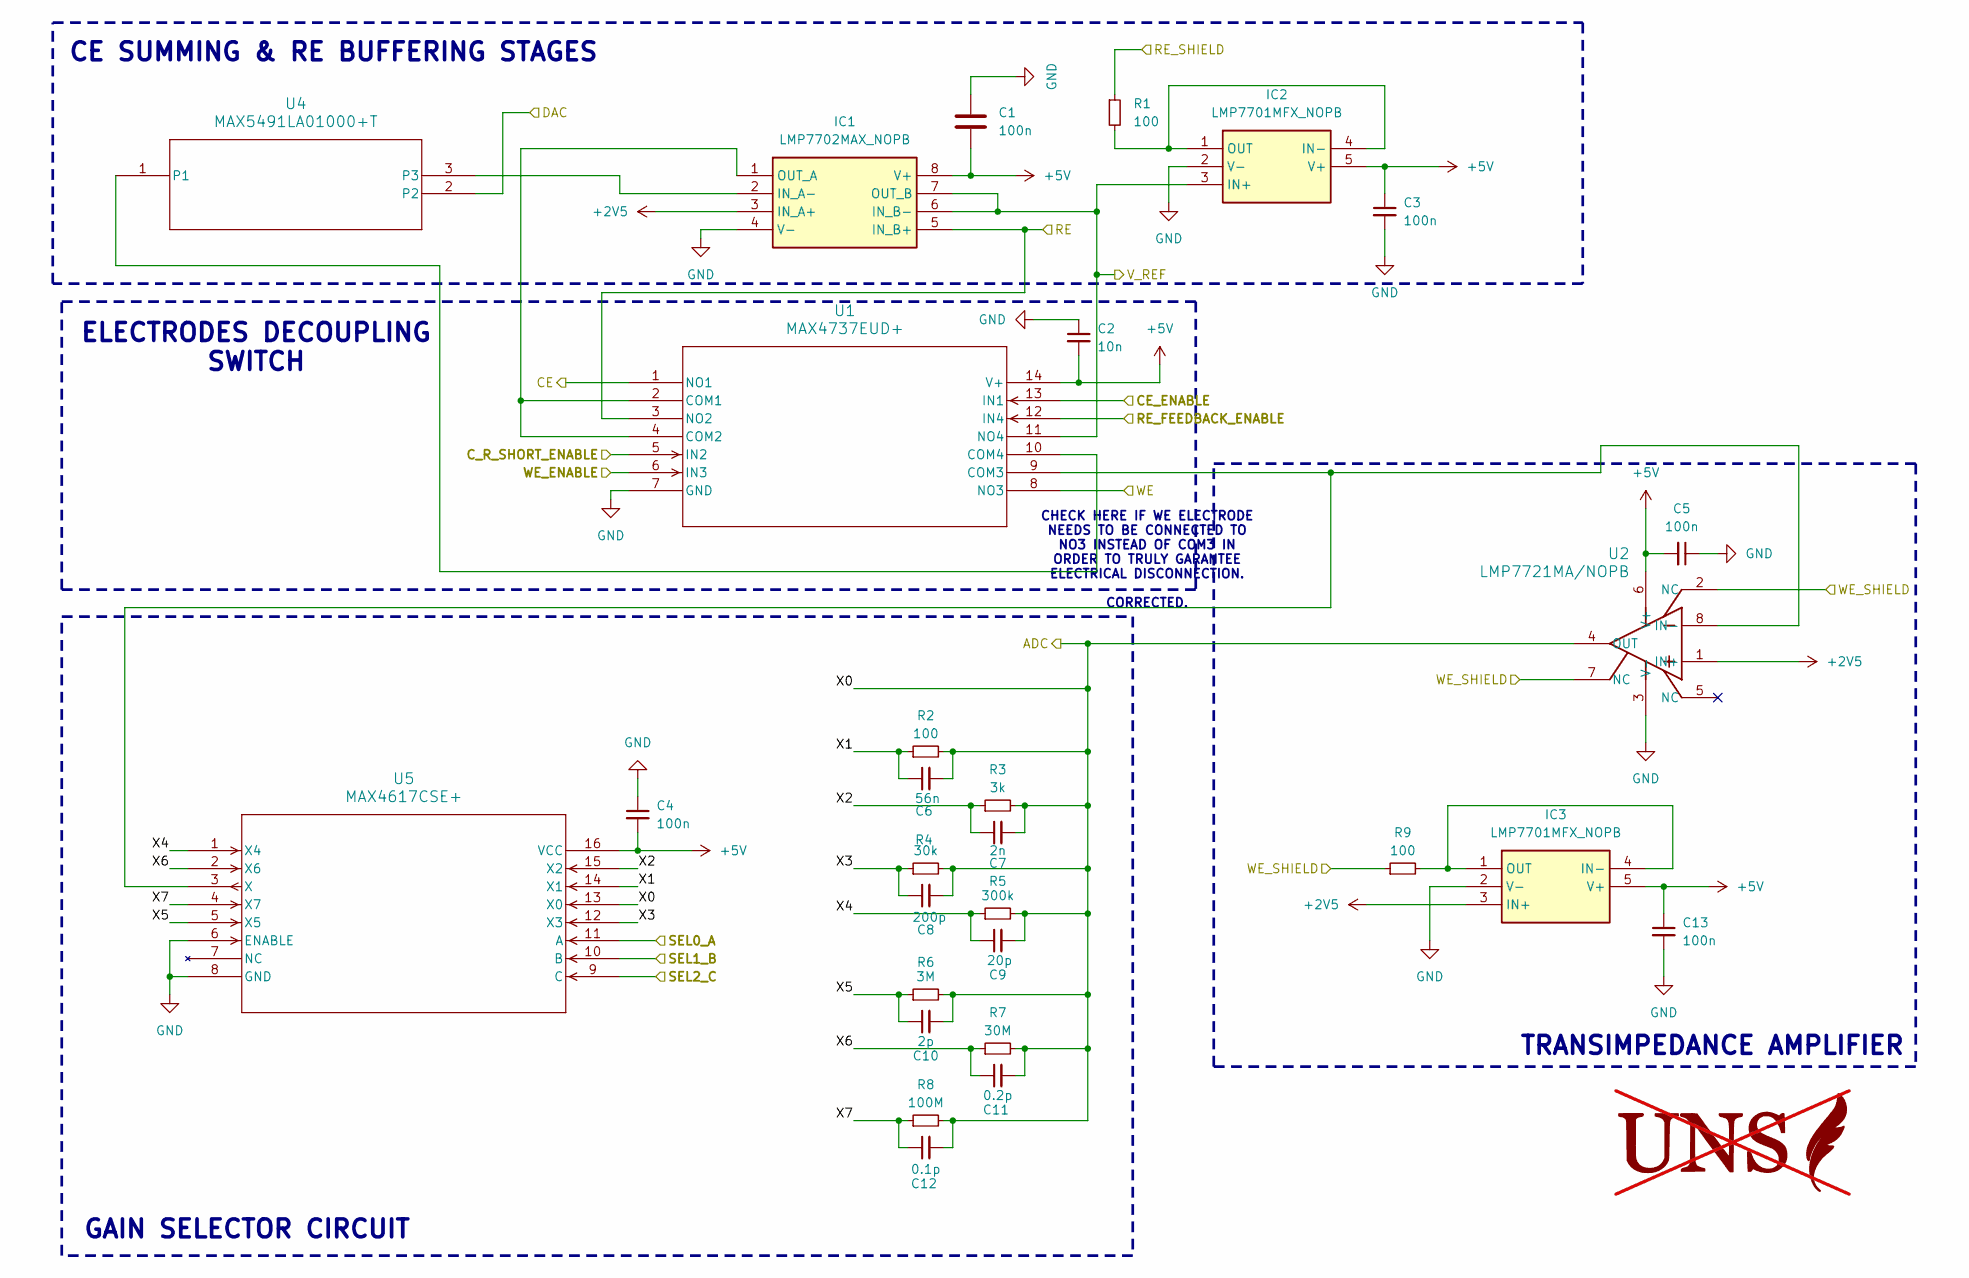
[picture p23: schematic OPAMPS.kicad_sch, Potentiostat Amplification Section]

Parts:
C1, C3, C4, C5, C13: 100n; C_0805_2012Metric_Pad1.18x1.45mm_HandSolder
C2: 10n; C_0805_2012Metric_Pad1.18x1.45mm_HandSolder
C6: 56n; C_0805_2012Metric_Pad1.18x1.45mm_HandSolder
C7: 2n; C_0805_2012Metric_Pad1.18x1.45mm_HandSolder
C8: 200p; C_0805_2012Metric_Pad1.18x1.45mm_HandSolder
C9: 20p; C_0805_2012Metric_Pad1.18x1.45mm_HandSolder
C10: 2p; C_0805_2012Metric_Pad1.18x1.45mm_HandSolder
C11: 0.2p; C_0805_2012Metric_Pad1.18x1.45mm_HandSolder
C12: 0.1p; C_0805_2012Metric_Pad1.18x1.45mm_HandSolder
IC1: LMP7702MAX_NOPB; SOIC127P600X175_LMP7702; MFR.Part # LMP7702MAX/NOPB
IC2, IC3: LMP7701MFX_NOPB; SOT95P280X145_LMP7701; MFR.Part # LMP7701MFX/NOPB
R1, R2, R9: 100; R_0805_2012Metric_Pad1.20x1.40mm_HandSolder
R3: 3k; R_0805_2012Metric_Pad1.20x1.40mm_HandSolder
R4: 30k; R_0805_2012Metric_Pad1.20x1.40mm_HandSolder
R5: 300k; R_0805_2012Metric_Pad1.20x1.40mm_HandSolder
R6: 3M; R_0805_2012Metric_Pad1.20x1.40mm_HandSolder
R7: 30M; R_0805_2012Metric_Pad1.20x1.40mm_HandSolder
R8: 100M; R_0805_2012Metric_Pad1.20x1.40mm_HandSolder
U1: MAX4737EUD+; MAX4737
U2: LMP7721MA/NOPB; M08ALMP7721_
U4: MAX5491LA01000+T; SOT23_5491
U5: MAX4617CSE+; MAX4617
U9: not fitted

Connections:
+2V5: IC1.3 (IN_A+), IC3.3 (IN+), U2.1 (IN+); also elsewhere on the board
+5V: C1.2, C2.2, C3.1, C4.2, C5.2, C13.1, IC1.8 (V+), IC2.5 (V+), IC3.5 (V+), U1.14 (V+), U2.6 (V+), U5.16 (VCC); also elsewhere on the board
/ADC: C6.2, C7.2, C8.2, C9.2, C10.2, C11.2, C12.2, R2.2, R3.2, R4.2, R5.2, R6.2, R7.2, R8.2, U2.4 (OUT), U5.13 (X0); also elsewhere on the board
/Amplifier Stage - Electrodes/X1: C6.1, R2.1, U5.14 (X1)
/Amplifier Stage - Electrodes/X2: C7.1, R3.1, U5.15 (X2)
/Amplifier Stage - Electrodes/X3: C8.1, R4.1, U5.12 (X3)
/Amplifier Stage - Electrodes/X4: C9.1, R5.1, U5.1 (X4)
/Amplifier Stage - Electrodes/X5: C10.1, R6.1, U5.5 (X5)
/Amplifier Stage - Electrodes/X6: C11.1, R7.1, U5.2 (X6)
/Amplifier Stage - Electrodes/X7: C12.1, R8.1, U5.4 (X7)
/CE: U1.1 (NO1); also elsewhere on the board
/CE_EN: U1.13 (IN1); also elsewhere on the board
/C_R_SHORT_EN: U1.5 (IN2); also elsewhere on the board
/DAC: U4.2; also elsewhere on the board
/RE: IC1.5 (IN_B+), U1.3 (NO2); also elsewhere on the board
/RE_FEEDBACK_EN: U1.12 (IN4); also elsewhere on the board
/RE_SHIELD: R1.1; also elsewhere on the board
/SEL_BIT0: U5.11 (A); also elsewhere on the board
/SEL_BIT1: U5.10 (B); also elsewhere on the board
/SEL_BIT2: U5.9 (C); also elsewhere on the board
/V_REF: IC1.6 (IN_B-), IC1.7 (OUT_B), IC2.3 (IN+), U1.11 (NO4); also elsewhere on the board
/WE: U1.8 (NO3); also elsewhere on the board
/WE_EN: U1.6 (IN3); also elsewhere on the board
/WE_SHIELD: R9.1, U2.2 (NC), U2.7 (NC); also elsewhere on the board
GND: C1.1, C2.1, C3.2, C4.1, C5.1, C13.2, IC1.4 (V-), IC2.2 (V-), IC3.2 (V-), U1.7 (GND), U2.3 (V-), U5.6 (ENABLE), U5.8 (GND); also elsewhere on the board
unnamed: IC1.2 (IN_A-), U4.3
unnamed: IC1.1 (OUT_A), U1.2 (COM1), U1.4 (COM2)
unnamed: IC2.1 (OUT), IC2.4 (IN-), R1.2
unnamed: IC3.1 (OUT), IC3.4 (IN-), R9.2
unnamed: U1.10 (COM4), U4.1
unnamed: U1.9 (COM3), U2.8 (IN-), U5.3 (X)

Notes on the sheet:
GAIN SELECTOR CIRCUIT
CE SUMMING & RE BUFFERING STAGES
CHECK HERE IF WE ELECTRODE NEEDS TO BE CONNECTED TO NO3 INSTEAD OF COM3 IN ORDER TO TRULY GARANTEE ELECTRICAL DISCONNECTION. CORRECTED.
TRANSIMPEDANCE AMPLIFIER
ELECTRODES DECOUPLING SWITCH

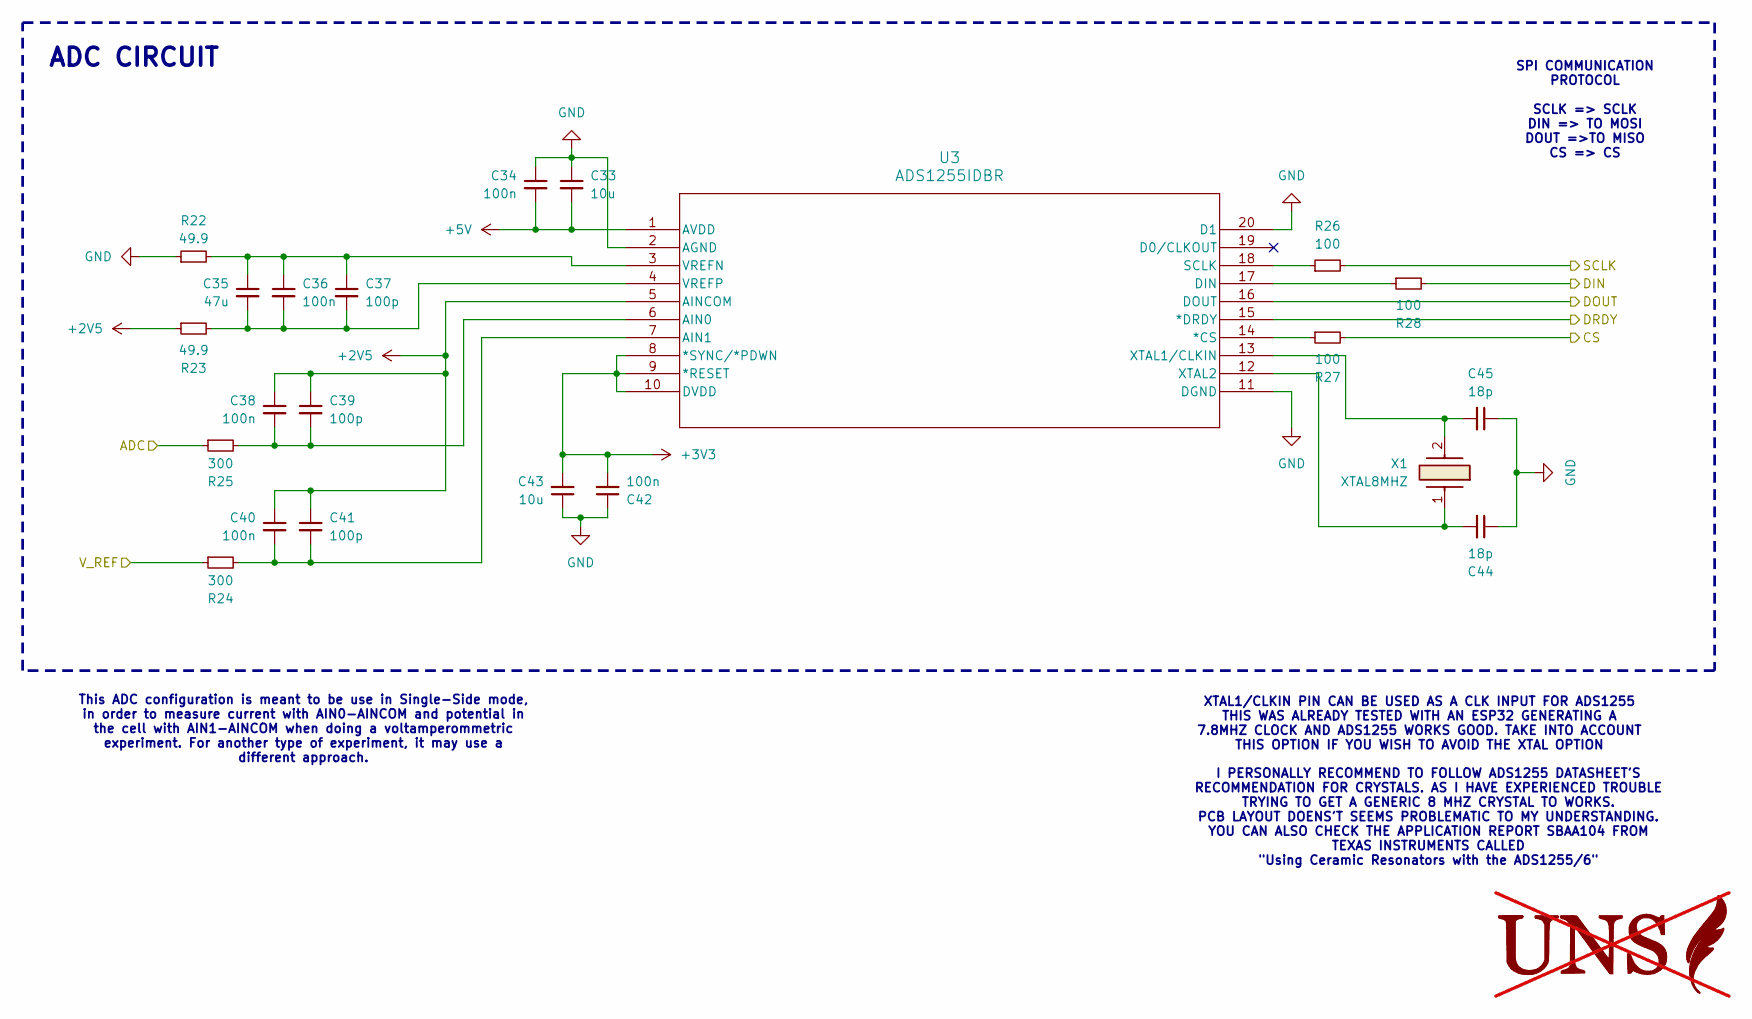
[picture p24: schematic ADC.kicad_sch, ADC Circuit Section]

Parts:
C33, C43: 10u; C_0805_2012Metric_Pad1.18x1.45mm_HandSolder
C34, C36, C38, C40, C42: 100n; C_0805_2012Metric_Pad1.18x1.45mm_HandSolder
C35: 47u; C_0805_2012Metric_Pad1.18x1.45mm_HandSolder
C37, C39, C41: 100p; C_0805_2012Metric_Pad1.18x1.45mm_HandSolder
C44, C45: 18p; C_0805_2012Metric_Pad1.18x1.45mm_HandSolder
R22, R23: 49.9; R_0805_2012Metric_Pad1.20x1.40mm_HandSolder
R24, R25: 300; R_0603_1608Metric_Pad0.98x0.95mm_HandSolder
R26, R27, R28: 100; R_0805_2012Metric_Pad1.20x1.40mm_HandSolder
U3: ADS1255IDBR; DB20_ADS1255
U12: not fitted
X1: XTAL8MHZ; CRYSTAL_8; MFR.Part # ECS-80-18-30Q-VY-TR

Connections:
+2V5: C38.1, C39.1, C40.1, C41.1, R23.1, U3.5 (AINCOM); also elsewhere on the board
+3V3: C42.2, C43.2, U3.8 (*SYNC/*PDWN), U3.9 (*RESET), U3.10 (DVDD); also elsewhere on the board
+5V: C33.2, C34.2, U3.1 (AVDD); also elsewhere on the board
/ADC: R25.1; also elsewhere on the board
/ADC_CS: R27.2; also elsewhere on the board
/ADC_DIN: R28.2; also elsewhere on the board
/ADC_DOUT: U3.16 (DOUT); also elsewhere on the board
/ADC_DRDY: U3.15 (*DRDY); also elsewhere on the board
/ADC_SCLK: R26.2; also elsewhere on the board
/V_REF: R24.1; also elsewhere on the board
GND: C33.1, C34.1, C42.1, C43.1, C44.1, C45.1, R22.1, U3.2 (AGND), U3.11 (DGND), U3.20 (D1); also elsewhere on the board
unnamed: R27.1, U3.14 (*CS)
unnamed: C38.2, C39.2, R25.2, U3.6 (AIN0)
unnamed: C40.2, C41.2, R24.2, U3.7 (AIN1)
unnamed: R28.1, U3.17 (DIN)
unnamed: R26.1, U3.18 (SCLK)
unnamed: C35.1, C36.1, C37.1, R22.2, U3.3 (VREFN)
unnamed: C35.2, C36.2, C37.2, R23.2, U3.4 (VREFP)
unnamed: C45.2, U3.13 (XTAL1/CLKIN), X1.2
unnamed: C44.2, U3.12 (XTAL2), X1.1

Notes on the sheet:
SPI COMMUNICATION PROTOCOL SCLK => SCLK DIN => TO MOSI DOUT =>TO MISO CS => CS
This ADC configuration is meant to be use in Single-Side mode, in order to measure current with AIN0-AINCOM and potential in the cell with AIN1-AINCOM when doing a voltamperommetric experiment. For another type of experiment, it may use a different approach.
XTAL1/CLKIN PIN CAN BE USED AS A CLK INPUT FOR ADS1255 THIS WAS ALREADY TESTED WITH AN ESP32 GENERATING A 7.8MHZ CLOCK AND ADS1255 WORKS GOOD. TAKE INTO ACCOUNT THIS OPTION IF YOU WISH TO AVOID THE XTAL OPTION
I PERSONALLY RECOMMEND TO FOLLOW ADS1255 DATASHEET'S RECOMMENDATION FOR CRYSTALS. AS I HAVE EXPERIENCED TROUBLE TRYING TO GET A GENERIC 8 MHZ CRYSTAL TO WORKS. PCB LAYOUT DOENS'T SEEMS PROBLEMATIC TO MY UNDERSTANDING. YOU CAN ALSO CHECK THE APPLICATION REPORT SBAA104 FROM TEXAS INSTRUMENTS CALLED "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
ADC CIRCUIT

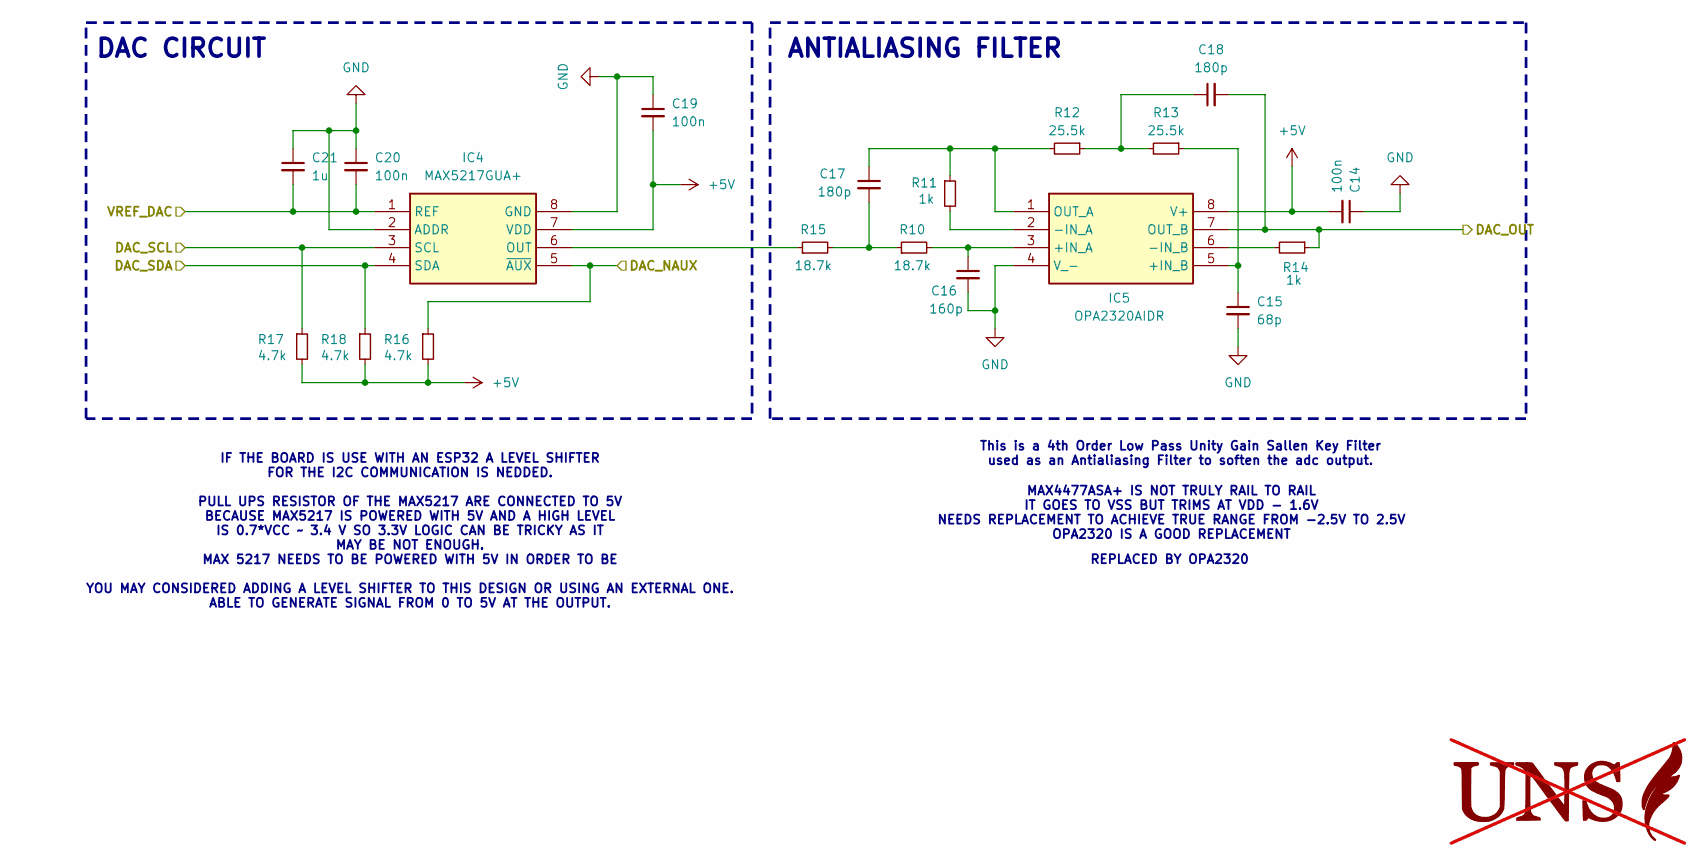
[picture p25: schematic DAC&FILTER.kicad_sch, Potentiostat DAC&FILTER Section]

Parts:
C14, C19, C20: 100n; C_0805_2012Metric_Pad1.18x1.45mm_HandSolder
C15: 68p; C_0805_2012Metric_Pad1.18x1.45mm_HandSolder
C16: 160p; C_0805_2012Metric_Pad1.18x1.45mm_HandSolder
C17, C18: 180p; C_0805_2012Metric_Pad1.18x1.45mm_HandSolder
C21: 1u; C_1206_3216Metric_Pad1.33x1.80mm_HandSolder
IC4: MAX5217GUA+; SOP65P490X110_MAX5217; MFR.Part # MAX5217GUA+
IC5: OPA2320AIDR; SOIC127P600X175-8N
R10, R15: 18.7k; R_0603_1608Metric_Pad0.98x0.95mm_HandSolder
R11, R14: 1k; R_0603_1608Metric_Pad0.98x0.95mm_HandSolder
R12, R13: 25.5k; R_0603_1608Metric_Pad0.98x0.95mm_HandSolder
R16, R17, R18: 4.7k; R_0603_1608Metric_Pad0.98x0.95mm_HandSolder
U10: not fitted

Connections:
+5V: C14.2, C19.2, IC4.7 (VDD), IC5.8 (V+), R16.2, R17.2, R18.2; also elsewhere on the board
/DAC: C18.2, IC5.7 (OUT_B), R14.1; also elsewhere on the board
/DAC_NAUX: IC4.5 (~AUX), R16.1; also elsewhere on the board
/DAC_SCL: IC4.3 (SCL), R17.1; also elsewhere on the board
/DAC_SDA: IC4.4 (SDA), R18.1; also elsewhere on the board
/REF5V: C20.2, C21.2, IC4.1 (REF); also elsewhere on the board
GND: C14.1, C15.2, C16.2, C19.1, C20.1, C21.1, IC4.2 (ADDR), IC4.8 (GND), IC5.4 (V_-); also elsewhere on the board
unnamed: C17.2, R10.1, R15.2
unnamed: C18.1, R12.1, R13.2
unnamed: IC4.6 (OUT), R15.1
unnamed: C16.1, IC5.3 (+IN_A), R10.2
unnamed: C15.1, IC5.5 (+IN_B), R13.1
unnamed: IC5.2 (-IN_A), R11.2
unnamed: IC5.6 (-IN_B), R14.2
unnamed: C17.1, IC5.1 (OUT_A), R11.1, R12.2

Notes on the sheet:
IF THE BOARD IS USE WITH AN ESP32 A LEVEL SHIFTER FOR THE I2C COMMUNICATION IS NEDDED. PULL UPS RESISTOR OF THE MAX5217 ARE CONNECTED TO 5V BECAUSE MAX5217 IS POWERED WITH 5V AND A HIGH LEVEL IS 0.7*VCC ~ 3.4 V SO 3.3V LOGIC CAN BE TRICKY AS IT MAY BE NOT ENOUGH. MAX 5217 NEEDS TO BE POWERED WITH 5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
ANTIALIASING FILTER
REPLACED BY OPA2320
MAX4477ASA+ IS NOT TRULY RAIL TO RAIL IT GOES TO VSS BUT TRIMS AT VDD - 1.6V NEEDS REPLACEMENT TO ACHIEVE TRUE RANGE FROM -2.5V TO 2.5V OPA2320 IS A GOOD REPLACEMENT
This is a 4th Order Low Pass Unity Gain Sallen Key Filter used as an Antialiasing Filter to soften the adc output.
DAC CIRCUIT

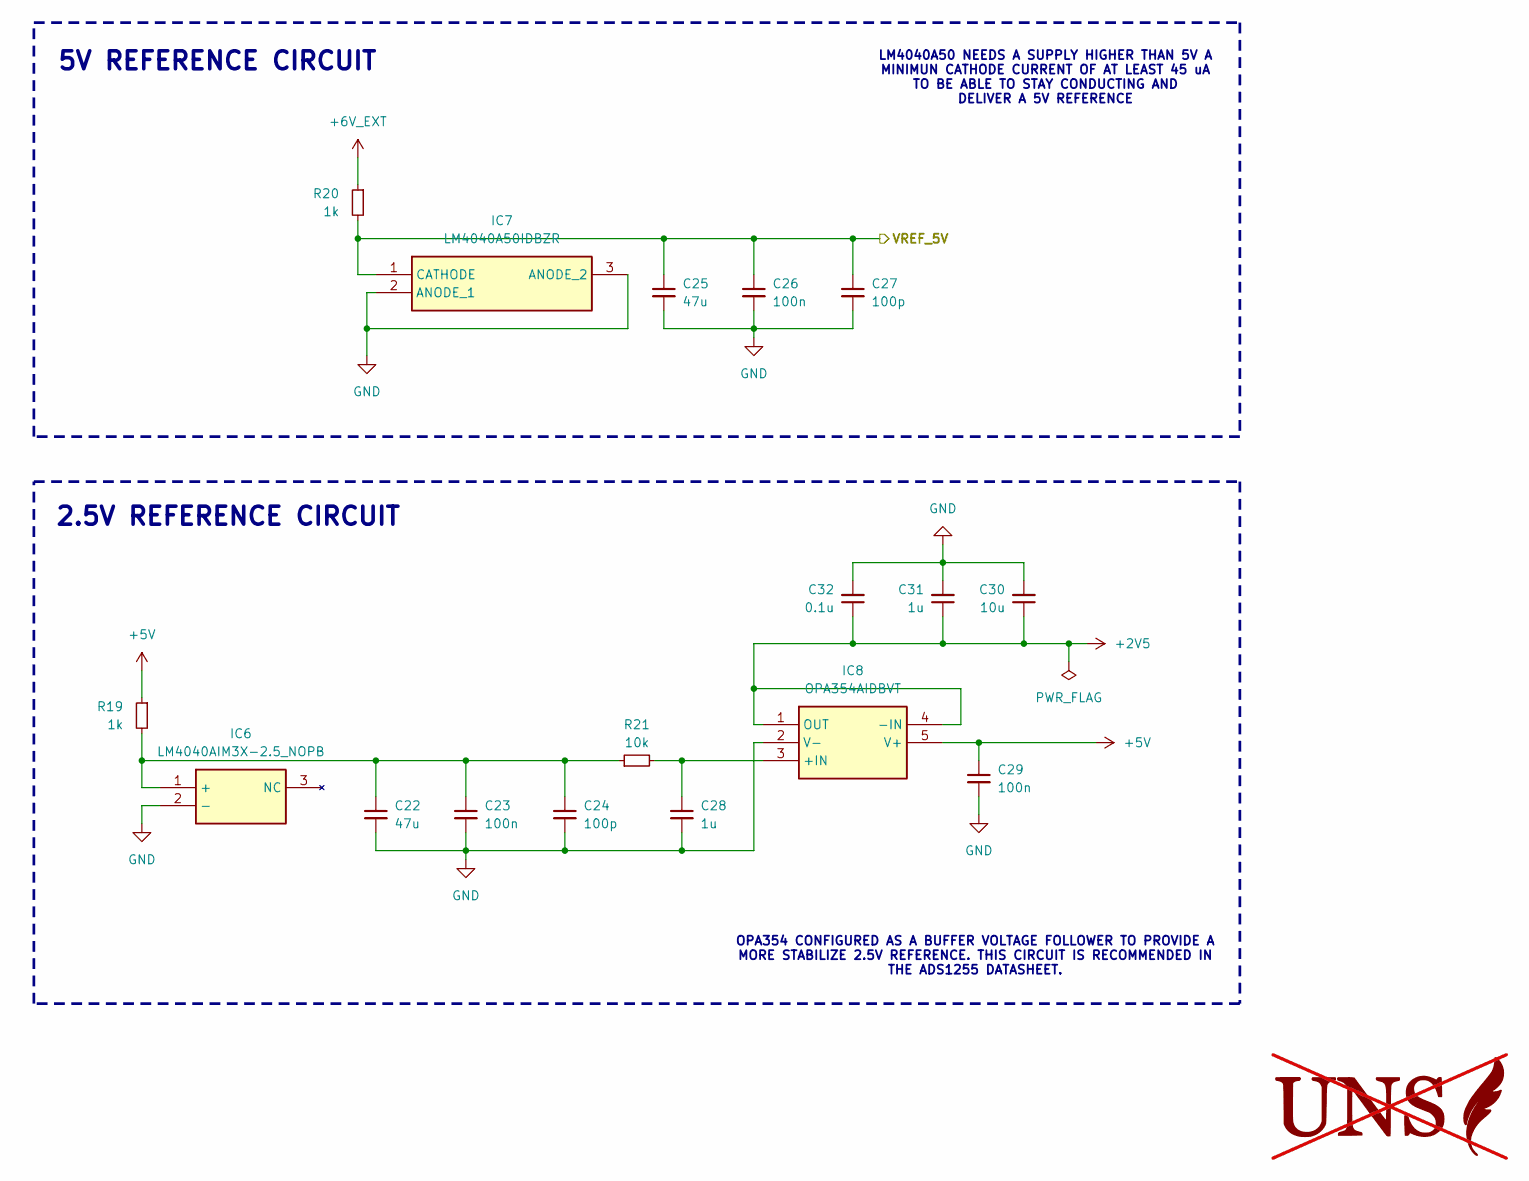
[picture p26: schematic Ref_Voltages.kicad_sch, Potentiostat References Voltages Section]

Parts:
C22, C25: 47u; C_0805_2012Metric_Pad1.18x1.45mm_HandSolder
C23, C26, C29: 100n; C_0805_2012Metric_Pad1.18x1.45mm_HandSolder
C24, C27: 100p; C_0805_2012Metric_Pad1.18x1.45mm_HandSolder
C28: 1u; C_1206_3216Metric_Pad1.33x1.80mm_HandSolder
C30: 10u; C_1206_3216Metric_Pad1.33x1.80mm_HandSolder
C31: 1u; C_0805_2012Metric_Pad1.18x1.45mm_HandSolder
C32: 0.1u; C_0805_2012Metric_Pad1.18x1.45mm_HandSolder
IC6: LM4040AIM3X-2.5_NOPB; SOT95P237X112_LM40402_5; MFR.Part # LM4040AIM3X-2.5/NOPB
IC7: LM4040A50IDBZR; SOT95P237X112_LM4040A5; MFR.Part # LM4040A50IDBZR
IC8: OPA354AIDBVT; SOT95P280X145_OPA354; MFR.Part # OPA354AIDBVT
R19, R20: 1k; R_0603_1608Metric_Pad0.98x0.95mm_HandSolder
R21: 10k; R_0603_1608Metric_Pad0.98x0.95mm_HandSolder
U11: not fitted

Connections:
+2V5: C30.1, C31.1, C32.1, IC8.1 (OUT), IC8.4 (-IN); also elsewhere on the board
+5V: C29.1, IC8.5 (V+), R19.1; also elsewhere on the board
+6V_EXT: R20.1; also elsewhere on the board
/REF5V: C25.1, C26.1, C27.1, IC7.1 (CATHODE), R20.2; also elsewhere on the board
GND: C22.2, C23.2, C24.2, C25.2, C26.2, C27.2, C28.2, C29.2, C30.2, C31.2, C32.2, IC6.2 (-), IC7.2 (ANODE_1), IC7.3 (ANODE_2), IC8.2 (V-); also elsewhere on the board
unnamed: C22.1, C23.1, C24.1, IC6.1 (+), R19.2, R21.1
unnamed: C28.1, IC8.3 (+IN), R21.2

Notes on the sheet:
5V REFERENCE CIRCUIT
OPA354 CONFIGURED AS A BUFFER VOLTAGE FOLLOWER TO PROVIDE A MORE STABILIZE 2.5V REFERENCE. THIS CIRCUIT IS RECOMMENDED IN THE ADS1255 DATASHEET.
LM4040A50 NEEDS A SUPPLY HIGHER THAN 5V A MINIMUN CATHODE CURRENT OF AT LEAST 45 uA TO BE ABLE TO STAY CONDUCTING AND DELIVER A 5V REFERENCE
2.5V REFERENCE CIRCUIT

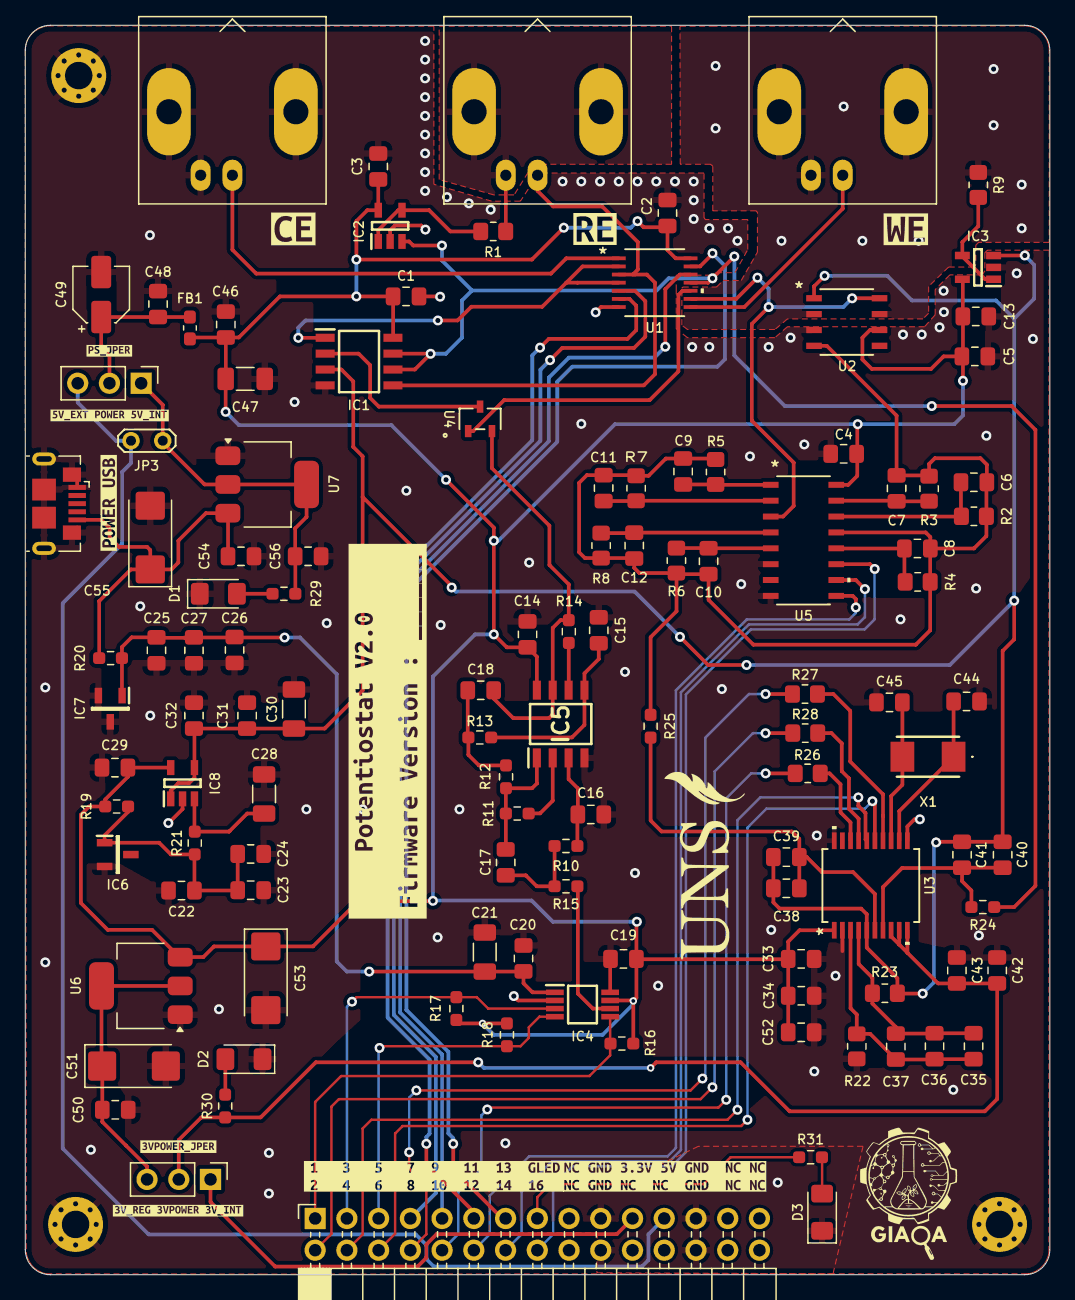
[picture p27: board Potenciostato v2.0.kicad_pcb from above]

Board: 2 copper layers, 82.0 x 100.0 mm, 129 parts (0 on the bottom side), 70 nets.

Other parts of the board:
kibuzzard-68ED1B67: G***; kibuzzard-68ED1B67
kibuzzard-68ED1EA7: G***; kibuzzard-68ED1EA7
kibuzzard-68ED1F3F: G***; kibuzzard-68ED1F3F
kibuzzard-68ED1F9A: G***; kibuzzard-68ED1F9A
kibuzzard-68ED1F51: G***; kibuzzard-68ED1F51
kibuzzard-68ED337E: G***; kibuzzard-68ED337E
kibuzzard-68ED3374: G***; kibuzzard-68ED3374
kibuzzard-68ED3386: G***; kibuzzard-68ED3386
kibuzzard-68ED3787: G***; kibuzzard-68ED3787
kibuzzard-68F13228: G***; kibuzzard-68F13228
kibuzzard-68F13266: G***; kibuzzard-68F13266

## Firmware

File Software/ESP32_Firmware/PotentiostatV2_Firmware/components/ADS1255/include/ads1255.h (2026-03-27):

/*******************************************************************************
 * @file        ads1255.h
 * @brief       C Header Library for ads1255/ads1256 family of Analog to Digital
 *              Conterters (ADC)
 * @details     This file contains the prototypes and definitions needed for 
 *              the library to implements the functionalities of the ADC.
 * @version     1.0
 * @author      Ing. Danilo Coletto Gallego
 * @date        04.12.2025
 * @copyright   (c) 2025  Universidad Nacional del Sur - CONICET
 * @see         
********************************************************************************
 * @note        Parts of this library are based on Simon Burkhardt STM32 Library 

MIT License

Copyright (c) 2020 Simon Burkhardt

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
THE SOFTWARE IS PROVIDED "AS IS", WITHOUT WARRANTY OF ANY KIND, EXPRESS OR
IMPLIED, INCLUDING BUT NOT LIMITED TO THE WARRANTIES OF MERCHANTABILITY,
FITNESS FOR A PARTICULAR PURPOSE AND NONINFRINGEMENT. IN NO EVENT SHALL THE
AUTHORS OR COPYRIGHT HOLDERS BE LIABLE FOR ANY CLAIM, DAMAGES OR OTHER
LIABILITY, WHETHER IN AN ACTION OF CONTRACT, TORT OR OTHERWISE, ARISING FROM,
OUT OF OR IN CONNECTION WITH THE SOFTWARE OR THE USE OR OTHER DEALINGS IN THE
SOFTWARE.
*/

#ifndef ADS1255_H
#define	ADS1255_H

#include "soc/spi_struct.h"
#include "soc/spi_reg.h"

#include "driver/spi_master.h"
#include "driver/ledc.h"
#include "general.h"
#include "esp_rom_sys.h"
#include "muxes.h"

//#define DEBUG_ADS1255

// reference voltage
#define ADS125X_VREF_2_5V (2.5f)
#define ADS125X_VREF_5_0V (5.0f)
#define ADS125X_OSC_FREQ_7_8M (7680000)
#define ADS125X_OSC_FREQ_8M (8000000)

#define ADS125X_ON          1
#define ADS125X_OFF         0


/*
const defaults = {
      clkinFrequency: 8000000,
      spiFrequency: 976563,
      spiMode: 1,
      vRef: 5.0,
    };
*/

// Configuración del SPI
#define SPI_HOST_ID             SPI2_HOST  // HSPI en ESP32
#define DMA_CHAN                SPI_DMA_CH_AUTO

// --- SPI SCLOCK SPEEDS ---
#define CLOCK_SPEED_100KHZ      100000
#define CLOCK_SPEED_250KHZ      250000
#define CLOCK_SPEED_500KHZ      500000
#define CLOCK_SPEED_1MHZ        1000000
#define CLOCK_SPEED_1_2MHZ      1200000
#define CLOCK_SPEED_1_5MHZ      1500000
#define CLOCK_SPEED_1_7MHZ      1700000
#define CLOCK_SPEED_1_92MHZ     1920000
#define CLOCK_SPEED_2MHZ        2000000

// --- ADS1255 PINOUT FOR ESP32 ---
#define GEN_CLOCK

#ifdef GEN_CLOCK
  #define ADS1255_CLOCK_PIN     GPIO_NUM_16 
#endif

#define ADS1255_DOUT_MISO       GPIO_NUM_19
#define ADS1255_DIN_MOSI        GPIO_NUM_23
#define ADS1255_SCLK            GPIO_NUM_18
#define ADS1255_CS              GPIO_NUM_5
#define ADS1255_DRDY            GPIO_NUM_4

// ADS1256 Register
#define ADS125X_REG_STATUS      0x00
#define ADS125X_REG_MUX         0x01
#define ADS125X_REG_ADCON       0x02
#define ADS125X_REG_DRATE       0x03
#define ADS125X_REG_IO          0x04
#define ADS125X_REG_OFC0        0x05
#define ADS125X_REG_OFC1        0x06
#define ADS125X_REG_OFC2        0x07
#define ADS125X_REG_FSC0        0x08
#define ADS125X_REG_FSC1        0x09
#define ADS125X_REG_FSC2        0x0A

// ADS1256 Command
// Datasheet p. 34 / Table 24
// All of the commands are stand-alone
// except for the register reads and writes (RREG, WREG) 
// which require a second command byte plus data

#define ADS125X_CMD_WAKEUP      0x00
#define ADS125X_CMD_RDATA       0x01
#define ADS125X_CMD_RDATAC      0x03
#define ADS125X_CMD_SDATAC      0x0f
#define ADS125X_CMD_RREG        0x10
#define ADS125X_CMD_WREG        0x50
#define ADS125X_CMD_SELFCAL     0xF0
#define ADS125X_CMD_SELFOCAL    0xF1
#define ADS125X_CMD_SELFGCAL    0xF2
#define ADS125X_CMD_SYSOCAL     0xF3
#define ADS125X_CMD_SYSGCAL     0xF4
#define ADS125X_CMD_SYNC        0xFC
#define ADS125X_CMD_STANDBY     0xFD
#define ADS125X_CMD_RESET       0xFE

#define ADS125X_BUFON           0x02
#define ADS125X_BUFOFF          0x00

#define ADS125X_CLKOUT_OFF      0x00
#define ADS125X_CLKOUT_1        0x20
#define ADS125X_CLKOUT_HALF     0x40
#define ADS125X_CLKOUT_QUARTER  0x60

#define ADS125X_RDATA           0x01    /* Read Data */
#define ADS125X_RDATAC          0x03    /* Read Data Continuously */
#define ADS125X_SDATAC          0x0F    /* Stop Read Data Continuously */
#define ADS125X_RREG            0x10    /* Read from REG */
#define ADS125X_WREG            0x50    /* Write to REG */
#define ADS125X_SELFCAL         0xF0    /* Offset and Gain Self-Calibration */
#define ADS125X_SELFOCAL        0xF1    /* Offset Self-Calibration */
#define ADS125X_SELFGCAL        0xF2    /* Gain Self-Calibration */
#define ADS125X_SYSOCAL         0xF3    /* System Offset Calibration */
#define ADS125X_SYSGCAL         0xF4    /* System Gain Calibration */
#define ADS125X_SYNC            0xFC    /* Synchronize the A/D Conversion */
#define ADS125X_STANDBY         0xFD    /* Begin Standby Mode */
#define ADS125X_RESET           0xFE    /* Reset to Power-Up Values */
#define ADS125X_WAKEUP          0xFF    /* Completes SYNC and Exits Standby Mode */

// multiplexer codes
#define ADS125X_MUXP_AIN0       0x00
#define ADS125X_MUXP_AIN1       0x10
#define ADS125X_MUXP_AIN2       0x20
#define ADS125X_MUXP_AIN3       0x30
#define ADS125X_MUXP_AIN4       0x40
#define ADS125X_MUXP_AIN5       0x50
#define ADS125X_MUXP_AIN6       0x60
#define ADS125X_MUXP_AIN7       0x70
#define ADS125X_MUXP_AINCOM     0x80

#define ADS125X_MUXN_AIN0       0x00
#define ADS125X_MUXN_AIN1       0x01
#define ADS125X_MUXN_AIN2       0x02
#define ADS125X_MUXN_AIN3       0x03
#define ADS125X_MUXN_AIN4       0x04
#define ADS125X_MUXN_AIN5       0x05
#define ADS125X_MUXN_AIN6       0x06
#define ADS125X_MUXN_AIN7       0x07
#define ADS125X_MUXN_AINCOM     0x08

// gain codes
#define ADS125X_PGA1            0x00
#define ADS125X_PGA2            0x01
#define ADS125X_PGA4            0x02
#define ADS125X_PGA8            0x03
#define ADS125X_PGA16           0x04
#define ADS125X_PGA32           0x05
#define ADS125X_PGA64           0x06

// data rate codes
/** @note: Data Rate vary depending on crystal frequency. 
  * Data rates listed below assumes the crystal frequency is 7.68Mhz
  * for other frequency consult the datasheet.
  */
#define ADS125X_DRATE_30000SPS  0xF0
#define ADS125X_DRATE_15000SPS  0xE0
#define ADS125X_DRATE_7500SPS   0xD0
#define ADS125X_DRATE_3750SPS   0xC0
#define ADS125X_DRATE_2000SPS   0xB0
#define ADS125X_DRATE_1000SPS   0xA1
#define ADS125X_DRATE_500SPS    0x92
#define ADS125X_DRATE_100SPS    0x82
#define ADS125X_DRATE_60SPS     0x72
#define ADS125X_DRATE_50SPS     0x63
#define ADS125X_DRATE_30SPS     0x53
#define ADS125X_DRATE_25SPS     0x43
#define ADS125X_DRATE_15SPS     0x33
#define ADS125X_DRATE_10SPS     0x23
#define ADS125X_DRATE_5SPS      0x13
#define ADS125X_DRATE_2_5SPS    0x03

// Struct "Object"
typedef struct {
    spi_device_handle_t hspix;
    float               vref;
    uint8_t             pga;
    uint8_t             current_drate;
    uint32_t            propagation_delay_us;
    float               convFactor;
    uint32_t            oscFreq;
    gpio_num_t          csPin;
    gpio_num_t          drdyPin;
} ADS125X_t;


typedef struct {
    uint8_t reg_val;      // Valor del registro DRATE (ej: 0x03 para 2.5 SPS)
    uint32_t timeout_us;  // Timeout recomendado en us
} ADS125X_timeout_t;


typedef struct {
    uint8_t reg_val;      // Valor del registro DRATE (ej: 0x03 para 2.5 SPS)
    uint32_t propagation_delay_us;  // Timeout recomendado en us
} ADS125X_prop_delay_t;

/**************Functions for ADS1255************/

uint8_t  ADS125X_CS                          (ADS125X_t *ads, uint8_t state);
uint8_t  ADS125X_DRDY_Wait                   (ADS125X_t *ads);
void     ADS125X_Init                        (ADS125X_t *ads, uint8_t drate, uint8_t gain, uint8_t buffer_en);
uint8_t  ADS125X_Register_Read               (ADS125X_t *ads, uint8_t reg, uint8_t* pData, uint8_t n);
uint8_t  ADS125X_Register_Write              (ADS125X_t *ads, uint8_t reg, uint8_t data);
uint8_t  ADS125X_CMD_Send                    (ADS125X_t *ads, uint8_t cmd);
void     ADS125X_ADC_Code2Volt               (ADS125X_t *ads, int32_t *pCode, float *pVolt, uint16_t size);
float    ADS125X_ADC_ReadVolt                (ADS125X_t *ads);
void     ADS125X_Channel_Set                 (ADS125X_t *ads, int8_t chan);
uint8_t  ADS125X_ChannelDiff_Set             (ADS125X_t *ads, int8_t p_chan, int8_t n_chan);
float    ADS125X_ADCFast_ReadVolt_HAL        (ADS125X_t *ads);
uint8_t  ADS125X_Set_Data_Rate               (ADS125X_t *ads, uint8_t drate);

float    ADS125X_Get_Prop_Delay_Us(void);
int32_t ADS125X_Get_Timeout_Us(uint8_t current_drate);

/*********Internal Functions for ADS1255*********/

spi_device_handle_t   init_spi_bus            (void);
void                  init_adc_clock          (uint32_t freq);
void                  ADS125X_Config_Pins     (void);

/*********HAL Layer Functions for ADS1255*********/

void     ADS125X_INIT_HAL           (uint8_t drate, uint8_t gain, uint8_t buffer_en);
void     ADS125X_WAKEUP_HAL         (void);
void     ADS125X_STANDBY_HAL        (void);
void     ADS125X_SDATAC_HAL         (void);
void     ADS125X_CMD_SEND_HAL       (uint8_t cmd);
float    ADS125X_READVOLT_HAL       (void);
uint8_t  ADS125X_READ_REG_HAL       (uint8_t reg, uint8_t* pData, uint8_t n);
void     ADS125X_WRITE_REG_HAL      (uint8_t reg, uint8_t data);
uint8_t  ADS125X_WAIT_DYDR_HAL      (void);
void     ADS125X_SET_DRATE_HAL      (uint8_t drate);



#endif	/* ADS1255_H */

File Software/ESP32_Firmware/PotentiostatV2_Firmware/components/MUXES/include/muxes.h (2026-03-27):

/*******************************************************************************
 * @file        muxes.h
 * @brief       C Library to control  Digital Muxes MAX4737EUD and MAX4617CSE+
 * @details     This file implements the functionalities of the Muxes
 * @version     1.0
 * @author      Ing. Danilo Coletto Gallego
 * @date        11.12.2025
 * @copyright   (c) 2025  Universidad Nacional del Sur - CONICET
 * @see         
******************************************************************************** 

MIT License
*/

#include "general.h"

#define     CONNECTED           1
#define     DISCONNECTED        0

// --- PINOUT MAX4617 FOR ESP32 ---

#define MAX4617_SEL_A       GPIO_NUM_27
#define MAX4617_SEL_B       GPIO_NUM_26
#define MAX4617_SEL_C       GPIO_NUM_25

// --- PINOUT MAX4737 FOR ESP32 ---

#define MAX4737_CR_SHORT_EN     GPIO_NUM_14
#define MAX4737_RE_FB_EN        GPIO_NUM_33
#define MAX4737_WE_EN           GPIO_NUM_13
#define MAX4737_CE_EN           GPIO_NUM_15

// --- GAIN VALUES ---

#define NO_GAIN				    0
#define GAIN1_100			    1
#define GAIN2_3K			    2
#define GAIN3_30K			    3
#define GAIN4_300K			    4
#define GAIN5_3M			    5
#define GAIN6_30M			    6
#define GAIN7_100M			    7


void MAX4617_Config_Pins    (void);
void MAX4617_Set_Gain       (int gain);
int MAX4617_get_gain        (void);


void MAX4737_Config_Pins    (void);

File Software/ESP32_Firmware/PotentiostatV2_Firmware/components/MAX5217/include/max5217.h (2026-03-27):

/*******************************************************************************
 * @file        max5217.h
 * @brief       C Header Library for MAX5217 Digital to Analog Converter
 * @details     This file implements the functionalities of the DAC.
 * @version     1.0
 * @author      Ing. Danilo Coletto Gallego
 * @date        04.12.2025
 * @copyright   (c) 2025  Universidad Nacional del Sur - CONICET
 * @see         
******************************************************************************** 
 */

#ifndef MAX5217_H
#define	MAX5217_H

#include <stdio.h>
#include "driver/i2c_master.h"
#include "general.h"


// Definiciones de pines (Ajústalo a tu placa)
#define MAX_5217_NAUX             GPIO_NUM_32
#define MAX_5217_SCL              GPIO_NUM_22
#define MAX_5217_SDA              GPIO_NUM_21
#define I2C_MASTER_FREQ_HZ        400000    // 100kHz o 400kHz

// DATOS DEL DAC
#define DAC1_DEVICE_ID 	            0x1C
#define DAC_REF_5V 		            5000
#define DAC_REF_2_5V 	            2500
#define MAX_VALUE_DAC	            65500


// COMANDOS DEL DAC
#define MAX5217_CMD_NO_OP 			0x00
#define MAX5217_CMD_CODE_LOAD 		0x01
#define MAX5217_CMD_CODE			0x02
#define MAX5217_CMD_LOAD			0x03
#define MAX5217_CMD_USER_CONFIG 	0x08
#define MAX5217_CMD_SW_RESET 		0x09
#define MAX5217_CMD_SW_CLEAR		0x10




/*********Internal Functions for ADS1255*********/
void                        I2C_Scanner              (i2c_master_bus_handle_t bus_handle);

/**************Functions for ADS1255************/

i2c_master_dev_handle_t     MAX5217_Setup_DAC        (uint8_t devID);
void                        MAX5217_Write_DAC_MV     (i2c_master_dev_handle_t dac_handle, float mvolt_value);
void                        MAX5217_Clear_DAC        (i2c_master_dev_handle_t dac_handle);

/*********HAL Layer Functions for ADS1255*********/

void        MAX5217_DAC_Setup_HAL       (void);
int         MAX5217_DAC_WRITE_HAL_MV    (float millivoltage);
void        MAX5217_DAC_CLEAR_HAL       (void);

#endif	/* MAX5217_H */

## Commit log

2025-10-19 Commit Inicial del Repositorio. Creacion de las Carpetas. Hardware Finalizado. No hay Software desarrollado.
    [ADC.kicad_sch, ADS1255.stp, BOM.xlsx, DAC&FILTER.kicad_sch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]
2025-12-17 Big commit. Hardware was already ready. Board arrived. Hardware testing phase and software development is ongoing, some hardware issues were detected and noted down in the KiCad project for future ve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
    [ADC.kicad_sch, DAC&FILTER.kicad_sch, OPAMPS.kicad_sch, Potenciostato v2.0.kicad_sch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]
2025-12-17 Hardware modifications. More notes added to the KiCad project related to hardware issues found during testing. USB Power and ground inverted corrected in design and PCB. MAX4477 replaced by OPA2320 i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
    [ADC.kicad_sch, DAC&FILTER.kicad_sch, OPA2320AIDR.stp, Potenciostato v2.0.kicad_pcb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]
2025-12-17 ADC, DAC, MUXES and GPIO libraries operational and working. There is still work to do and further commplementary functions to implement but the basics are ready and functional. Is necessary to implem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
2025-12-17 New README update
    [Potenciostato v2.0.kicad_sch]
2025-12-22 Further documentation and notes on the schematic. Software updates: In MAX4617, corrections in write function, more robust code verification to prevent overflows. In MUX, correction to MAX4617 gain c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
    [ADC.kicad_sch, DAC&FILTER.kicad_sch, OPAMPS.kicad_sch, Potenciostato v2.0.kicad_sch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]
2026-02-06 ADS1255 datasheet added. ADS1255 example libraries for STM32 also added.
2026-02-25 No changes in hardware. New
    [first_test_from_esp32.csv]
2026-02-27 Hardware: Hardware Corrections in Potentiostat, small but important ones (WE electrode, Normal Open connection for electric disconnection in schematic and PCB. DAC I2C pull up resistors connected to 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
    [ADC.kicad_sch, DAC&FILTER.kicad_sch, ESP32_Board.kicad_pcb, ESP32_Board.kicad_sch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]
2026-03-03 Se resolvieron multiples incovenientes criticos en la interfaz y el backend. Principalmente, problemas que ralentizaban la lecturas de las muestras asociados con las graficas. Se agregaron tasas de r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
    [ESP32_Board.kicad_pcb, ESP32_Board.kicad_sch, bom.csv, designators.csv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]
2026-03-04 Interfaz actualizada. Implementacion del viewer para visualizar graficas, optimizacion final con filtros sobre los datos. Funcionalidad al 100%. Pequeños fixes por el camino, version estable y practi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
2026-03-05 Physical Disconnection Device Detection added to UI. Preconditioning treatment implemented in firmware and small fixes related to it. Other smalls fixes in UI related to new featured implemented. UI 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
    [CET-C1.csv, CET-C1s.csv, CET-C2.csv, CET-C2s.csv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]
2026-03-09 CPE fully incorporated and implemented in firmwared and software. Data display updated and upgrated with auto scale selector. 3D design files for case added.
    [Potentiostat_Case.f3d, STL_Pot_Bot_Case2.stl, STL_Pot_Top_Case2.stl]
2026-03-27 ESP32 Board 5V pinout correction
    [ESP32_Board.kicad_pcb, ESP32_Board.kicad_sch]

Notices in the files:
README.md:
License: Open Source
